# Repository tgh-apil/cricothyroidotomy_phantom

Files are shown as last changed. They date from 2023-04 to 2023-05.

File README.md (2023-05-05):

# Cricothyroidotomy Phantom

A cricothyroidotomy training phantom, created using 3D printing and ballistics gel molding. Intended for practice in locating the cricothyroid membrane and creating an incision through it. See purchasing information and maintenance and assembly instructions below.

This model was developed at the [Lynn & Arnold Irwin Advanced Perioperative Imaging Lab](https://apil.ca/), Toronto General Hospital, University Health Network.

> <br>
> Fully assembled phantom.

## Purchasing Information

To purchase this phantom, please email <apil@uhn.ca> and a representative will be in touch with you with more details.

**A purchased phantom contains the following**:

1. APIL Cricothyroidotomy Phantom base
2. 10 x gel overlays
3. 10 x fully assembled insert rings

## Care and Maintenance
Store gel overlays in a bag or box when not in use to prevent tearing from excessive handling. Once an overlay is placed on a phantom and used (i.e. cut into), it can be replaced with another. If more gel overlays are desired, the gel can be remelted and cast to form new overlays by following the assembly instructions below.

A used insert ring can be replaced with another, or can be reused by rewrapping the ring with duct tape.

## Parts, Materials & Equipment
### Parts List
> 

#### Printed Parts
* base — cricothyroidotomy base.stl
* molding insert* — cricothyroidotomy molding insert.stl
* insert — cricothyroidotomy ring.stl
* intermediate mold part 1** — intermediate mold 1.stl
* intermediate mold part 2** — intermediate mold 2.stl

Files are available for download [here](https://github.com/tgh-apil/cricothyroidotomy_phantom/tree/main/stl%20files).

\* ***Print the molding insert with HTPLA or another heat resistant 3D printing filament. The other components can be printed with any kind of rigid plastic.***

\** A portion of these components were modified from NIOSH National Personal Protective Technology Laboratory (NPPTL)’s ISO Digital Headforms (specifically the medium size): https://www.cdc.gov/niosh/npptl/topics/respirators/headforms/default.html

#### Other
* Duct tape
* 4 M3 screws

### Materials
* High temperature PLA, or another 3D printing filament with heat-resistant properties
* Optional other filament (PLA recommended)
* Ballistics gel (https://www.clearballistics.com/shop/20-ballistic-gelatin-nato-block-16x6x6/, https://humimic.com/product/gelatin-4-medical-gel-by-the-pound/)
* Graphite powder
* Smooth-On’s Dragon Skin 30A Silicone Rubber, or another silicone of similar hardness (https://www.smooth-on.com/products/dragon-skin-30/)

### Equipment
* 3D printer
* Degassing chamber 
* Crock pot, or another method of melting the ballistics gel

## Assembly Instructions
**CAUTION**: Use appropriate heat-proof gloves when working with liquefied ballistic gel and/or heat gun.<br>
**CAUTION**: Work **only** in a very well ventilated area. A fumehood is *highly* recommended.

1. Print out the printed components, using a heat-resistant filament for the molding insert, and any kind of rigid plastic for the other components.
2. Use four M3 screws to attach the two intermediate mold components together. Seal off the seams with clay or hot glue. Prepare, degas, and pour roughly 750mL of Smooth-On’s Dragon Skin 30A Silicone Rubber (or another silicone of similar hardness) into the intermediate mold. Once cured, remove the silicone mold from the intermediate mold.
3. Seal off the molding insert to prevent ballistics gel from entering the inside of the insert. Here this was done with a taped insert and silicone.
> <br>
> Molding insert, sealed off with tape and silicone.
4. Melt 80 g of ballistics gel (here, a roughly 2:1 mixture of [20% ballistics gel](https://www.clearballistics.com/shop/20-ballistic-gelatin-nato-block-16x6x6/) and [Humimic Medical Ballistics Gel #4](https://humimic.com/product/gelatin-4-medical-gel-by-the-pound/) was used) in a crockpot at 105C - 115C (approx. 225F - 240F).
5. Stir graphite powder into liquefied gel until saturated and uniformly distributed.
6. Pour roughly 75 g of ballistics gel into the mold then insert the molding insert. The top of the insert should be just above the top of the mold.
> <br>
> Gel molding process. The sides of the mold have been clamped here to ensure the mold retains its shape.
7. Wait until gel cools (~45 min) then remove the insert. Cut off the overlapping edges and peel the gel off the insert carefully. Ensure there are no holes around the area of incision.
> <br>
> Left: post-molding results. Right: gel peeled off of molding insert.
8. Wrap the insert twice with duct tape and place inside the base, aligning the insert’s hole with the incision site. Place the gel onto the cricothyroidotomy base.
> <br>
> Assembled phantom.

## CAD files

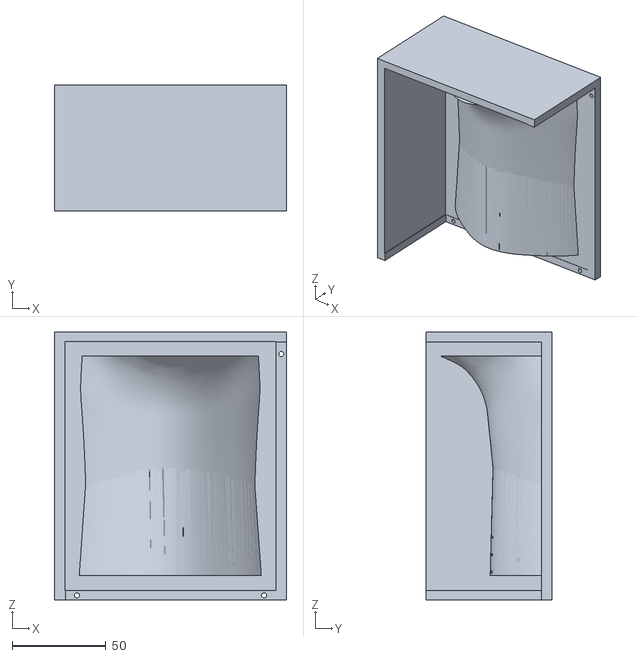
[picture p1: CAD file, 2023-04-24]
stl files/intermediate mold 1.stl
124.1 x 67.1 x 143.2

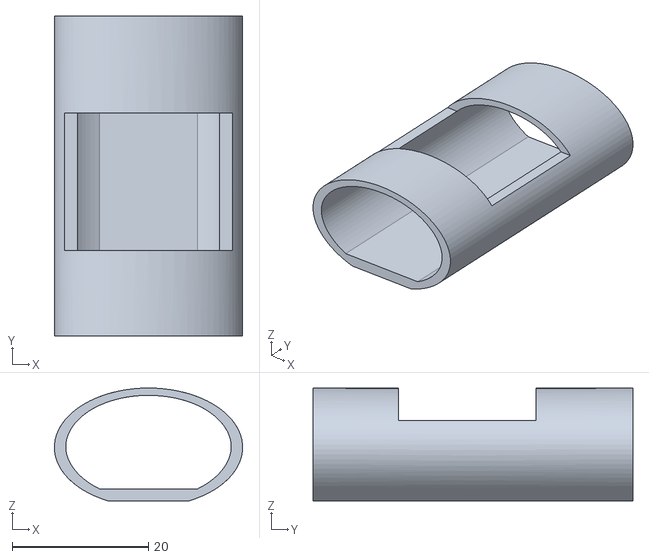
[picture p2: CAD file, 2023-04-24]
stl files/cricothyroidotomy ring.stl
27.6 x 47.0 x 16.6

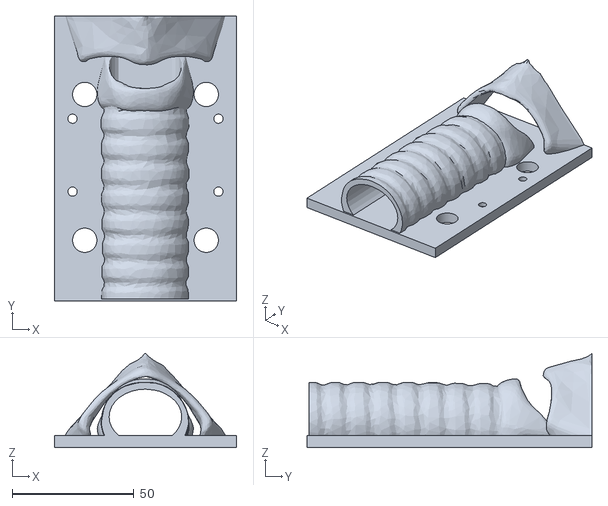
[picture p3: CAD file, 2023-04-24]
stl files/cricothyroidotomy molding insert.stl
75.0 x 117.3 x 38.8

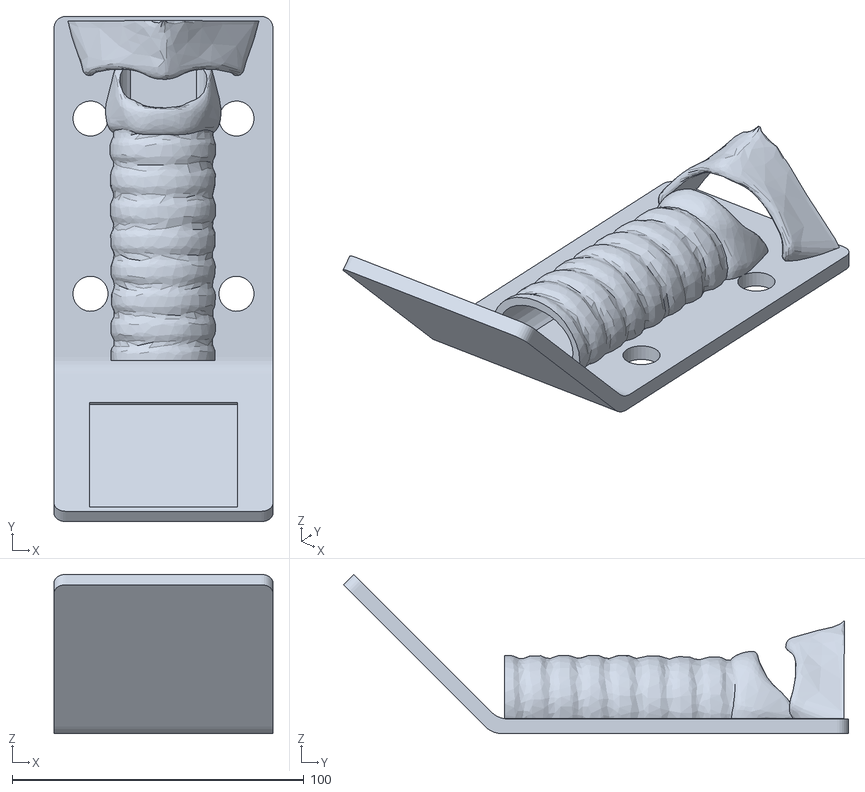
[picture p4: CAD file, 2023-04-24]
stl files/cricothyroidotomy base.stl
75.0 x 173.0 x 54.5

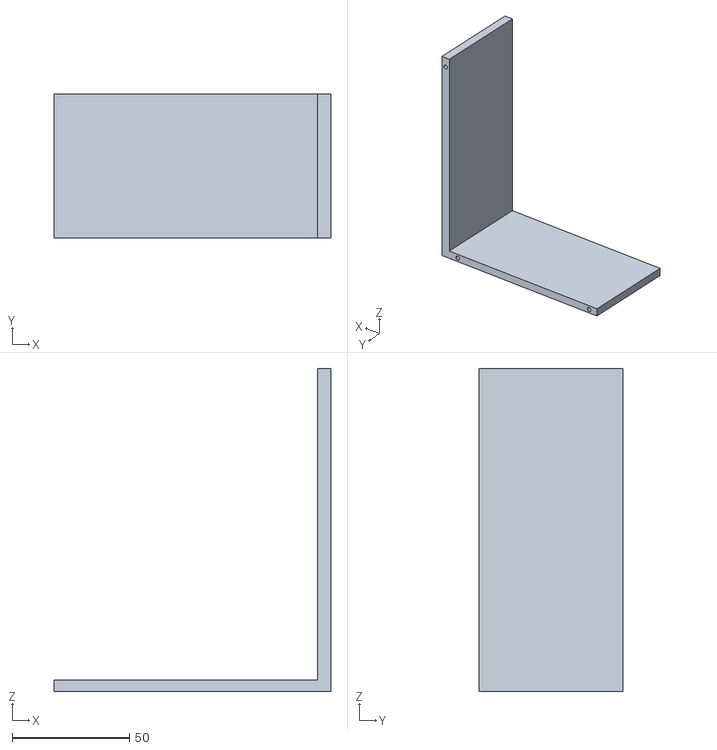
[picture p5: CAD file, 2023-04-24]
stl files/intermediate mold 2.stl
118.0 x 61.5 x 137.9
